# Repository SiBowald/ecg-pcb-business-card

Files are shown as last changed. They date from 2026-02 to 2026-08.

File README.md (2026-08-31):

# ECG PCB Business Card

## Table of contents

- [ECG PCB Business Card](#ecg-pcb-business-card)
  - [Intended use / disclaimer](#intended-use--disclaimer)
  - [Battery safety](#battery-safety)
  - [What the card does](#what-the-card-does)
  - [Compatibility (important)](#compatibility-important)
  - [Quick start (battery recommended)](#quick-start-battery-recommended)
  - [How to hold it (signal quality)](#how-to-hold-it-signal-quality)
  - [Powering via NFC energy harvesting (Android only)](#powering-via-nfc-energy-harvesting-android-only)
  - [What you should see](#what-you-should-see)
  - [Files & documentation](#files--documentation)
    - [Project structure](#project-structure)
    - [Running the web app locally](#running-the-web-app-locally)
  - [Quick troubleshooting](#quick-troubleshooting)
  - [Key ICs used](#key-ics-used)
  - [License](#license)
  - [Sponsorship](#sponsorship)

Educational demo: a functional single-lead ECG front end on a business-card-sized PCB.  
It streams the signal to your phone or computer using frequency-modulated ultrasound, decoded in a browser-based web app.

Goal: power it up, open the web app, and see a clean ECG-like waveform within about a minute, without any special lab setup.

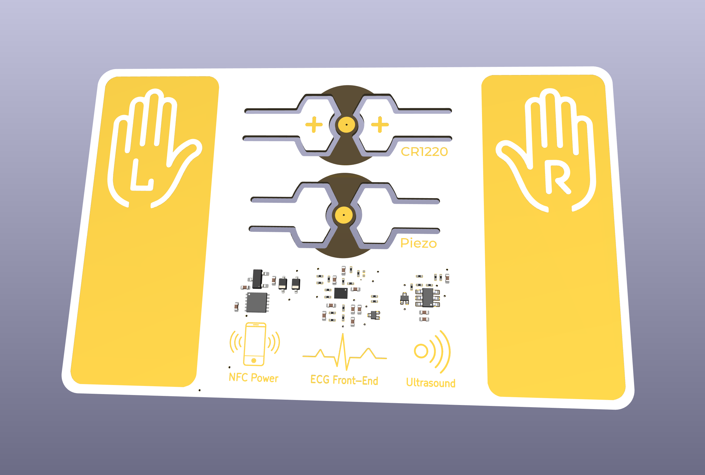
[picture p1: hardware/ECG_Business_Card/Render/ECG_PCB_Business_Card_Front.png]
ECG PCB Business Card - Front

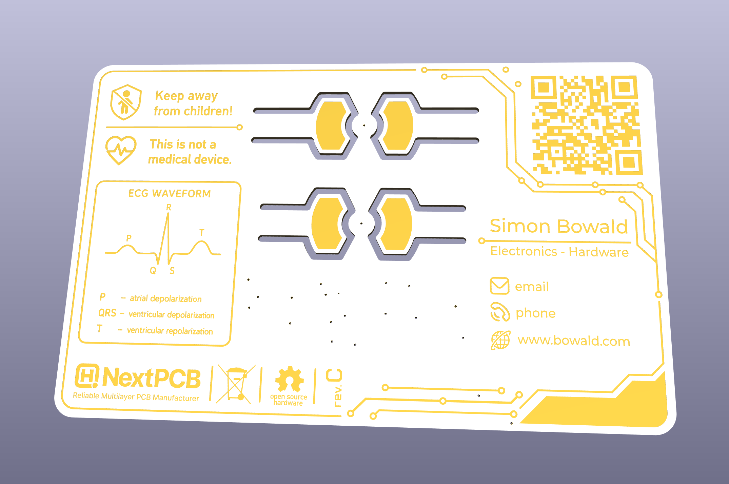
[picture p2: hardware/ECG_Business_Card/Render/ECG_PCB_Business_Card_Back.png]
ECG PCB Business Card - Front

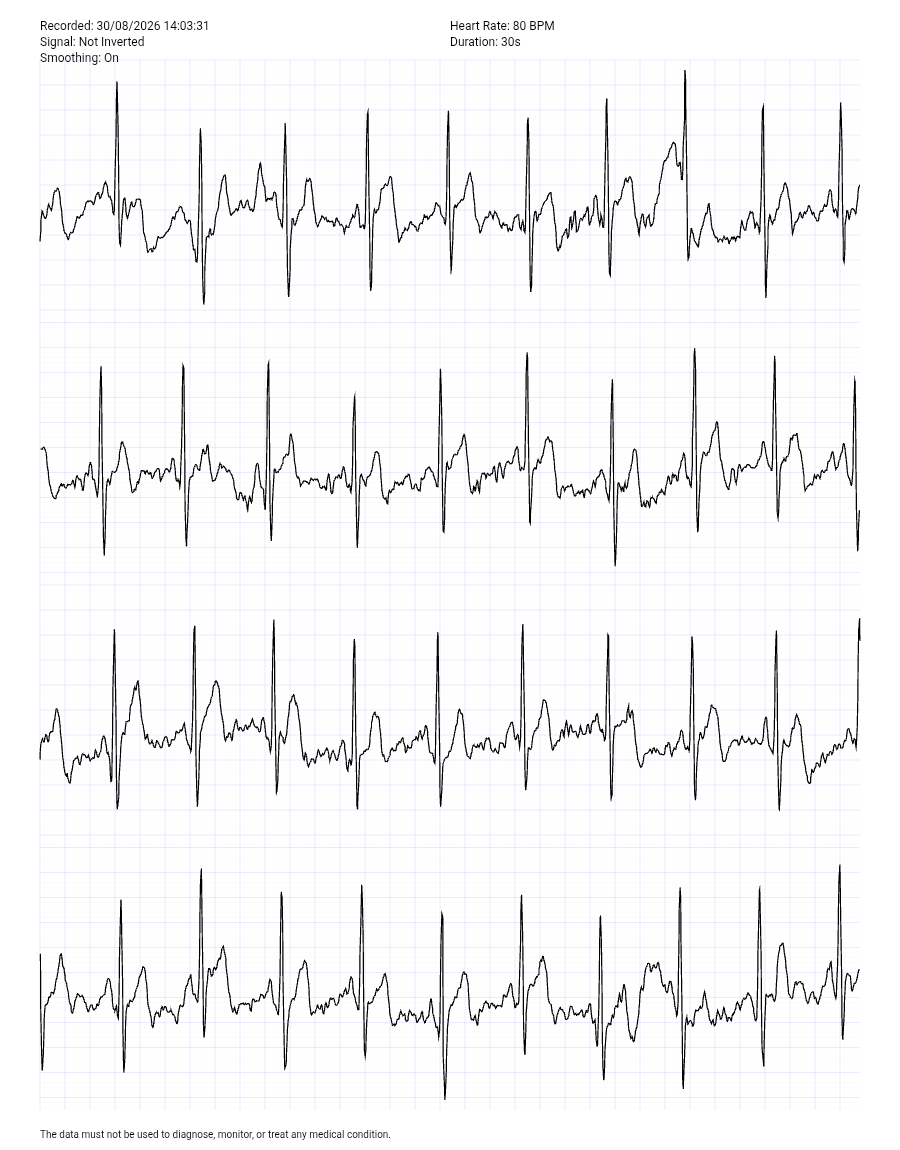
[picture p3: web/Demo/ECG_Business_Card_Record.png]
ECG PCB Business Card - Record


---

## Intended use / disclaimer

**This is a DIY educational demo and not a medical device.**  
It is not intended for diagnosis, monitoring, or clinical decisions.

---

## Battery safety

The CR1220 coin cell may be outside of its original packaging. Coin cell batteries are hazardous if swallowed, so **keep them away from children at all times**.

---

## What the card does

- Measures a single-lead ECG using the built-in left/right finger pads
- Streams the signal to a web application via **ultrasound** (microphone permission required)
- Power options:
  - **Battery (recommended)**
  - **NFC energy harvesting (Android only)**

---

## Compatibility (important)

- **iOS:** works best with **Safari**
- **Android:** works best with **Chrome**
- **NFC energy harvesting:** works **only on Android**
  - iOS does not provide a reliable continuous NFC power mode for this use
- If powering via NFC energy harvesting, the phone **must not be charging** (unplug it)

---

## Quick start (battery recommended)

1. **Insert a 3 V CR1220 battery** (rated for at least **500 µA continuous load**).  
   Ensure the **+ (positive) side** faces the same direction as the **+** symbols on the PCB.  
   Do not bend the arms of the PCB battery holder more than necessary.  
   Idle current is **below 1 µA**, so the battery can be left in the holder.

2. **Open the web app**
   - Easiest: tap the phone to the card to open the link (NFC enabled + phone unlocked)
   - Scan the printed QR code
   - Or run locally (see **Files & documentation** below)

3. **In the web application**
   - Press **Start**
   - Allow **microphone access** when prompted

---

## How to hold it (signal quality)

- Place the phone/laptop on a table and rest your elbows to reduce motion.
- Hold the card firmly and press your thumbs onto the pads:
  - Left thumb on the pad marked with the hand icon and **“L”**
  - Right thumb on the pad marked with the hand icon and **“R”**
- Stay still and relax your hands and shoulders (movement causes artifacts).
- Keep the phone close to the card so the microphone picks up the signal reliably.
- Use a quiet room if possible (avoid talking, music, fans, strong background noise).
- Avoid Bluetooth headsets so the browser uses the built-in microphone.

---

## Powering via NFC energy harvesting (Android only)

Use this when you want a “no battery” demo. It is more sensitive to positioning.

1. Make sure the phone is **not charging** (unplug it).
2. Place the card on the **back of the phone**, centered over the phone’s **NFC coil** area.
3. Flip the card upside down as needed so Left/Right orientation is correct while it sits on the phone.
4. Press fingers on the same **L** and **R** pads as in battery mode.
5. If your phone has a metal frame/back, avoid touching metal parts while contacting the pads.

---

## What you should see

You should see a waveform similar to the example printed on the back of the card (below “This is not a medical device.”).

If the signal looks noisy or flat, it is almost always due to:
- Contact pressure
- Hand motion
- Dry skin
- NFC positioning (in harvesting mode)

---

## Files & documentation

### Project structure

- `hardware/ECG_Business_Card/`  
  KiCad project including the schematic, PCB layout, manufacturing files, and documentation assets.

- `web/`  
  Browser-based ECG decoder and viewer.

### Web app

The ECG monitor can be used either locally or directly through GitHub Pages.

**Online:**  
[Open the Ultrasound-based ECG Monitor](https://sibowald.github.io/ecg-pcb-business-card/)

**Locally:**  
Open `web/ultrasound-ecg-monitor/index.html` in a modern web browser.

Microphone access is required for the ECG monitor.

---

## Quick troubleshooting

### No signal / flat line
- Confirm battery orientation (+ matches PCB)
- Press **Start**
- Ensure the browser has **microphone permission**
- Keep the phone very close and ensure it uses the **built-in mic** (disconnect Bluetooth devices)
- Audio sanity check: clapping near the phone should cause a visible change in the signal

### Very noisy signal
- Stay still, increase thumb pressure slightly, relax shoulders
- Try a quieter room
- Dry skin reduces contact: slightly moist fingertips can help
- Avoid touching metal parts of the phone while contacting the pads

### NFC power issues (Android)
- Phone must be unplugged (not charging)
- Align the card over the NFC coil and try small position shifts
- Remove thick cases

---

## Key ICs used

- **AD8233** – Single-lead ECG analog front end (instrumentation amp + filters) used to acquire the ECG signal from the finger pads.
- **LTC6990** – Timer/VCO used to generate the FM ultrasound carrier/modulation for audio-band transmission.
- **ST25DV** – NFC tag used for tap-to-open link and NFC energy harvesting support.

---

## License

See `LICENSE`.

---

## Sponsorship

### Rev. C – Supported by NextPCB

Revision C of the **ECG PCB Business Card** was kindly sponsored by **NextPCB**, who supported the PCB manufacturing and assembly of this revision.

Thank you to NextPCB for supporting this project!

<p align="center">
  <a href="https://www.nextpcb.com/">
    NextPCB
  </a>
</p>

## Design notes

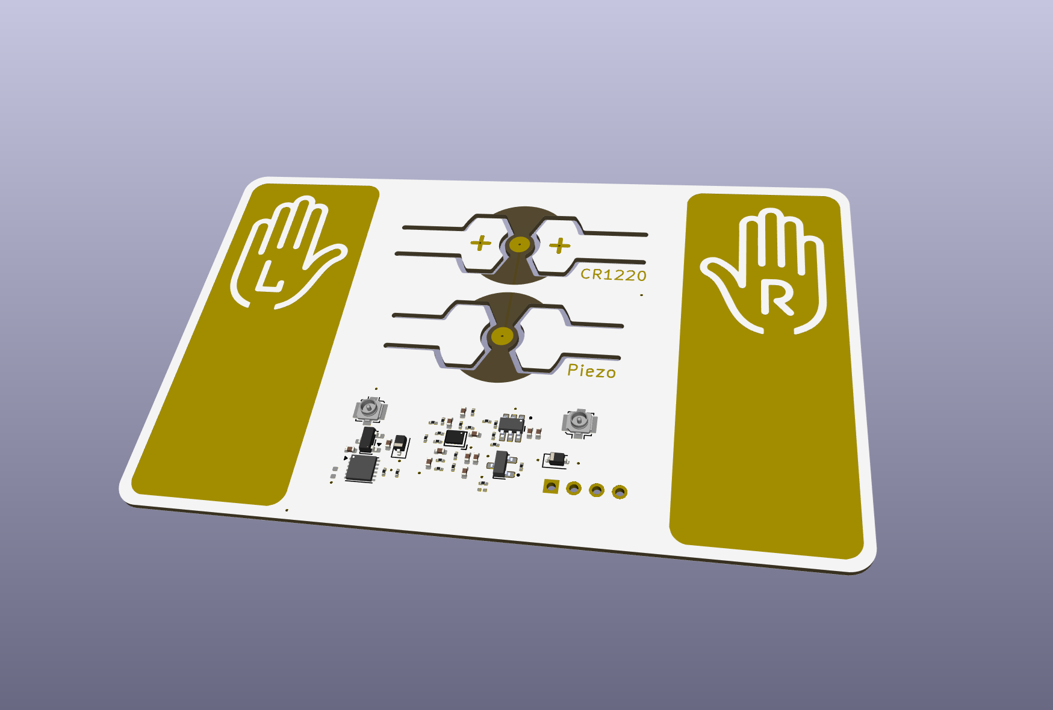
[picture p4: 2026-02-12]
hardware/ECG_Business_Card_v3/Render/ECG_PCB_Business_Card_Front.png

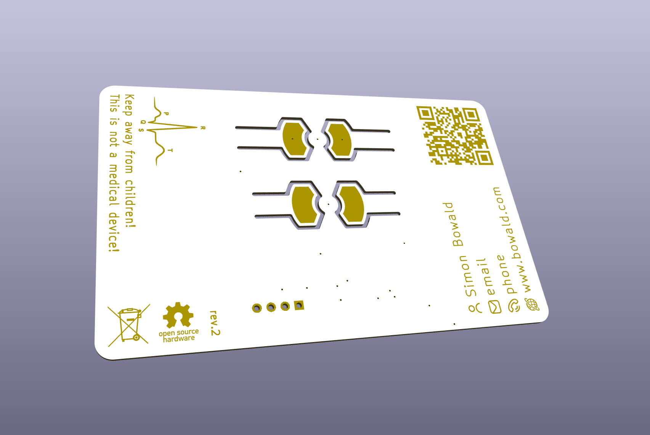
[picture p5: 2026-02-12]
hardware/ECG_Business_Card_v3/Render/ECG_PCB_Business_Card_Back.png

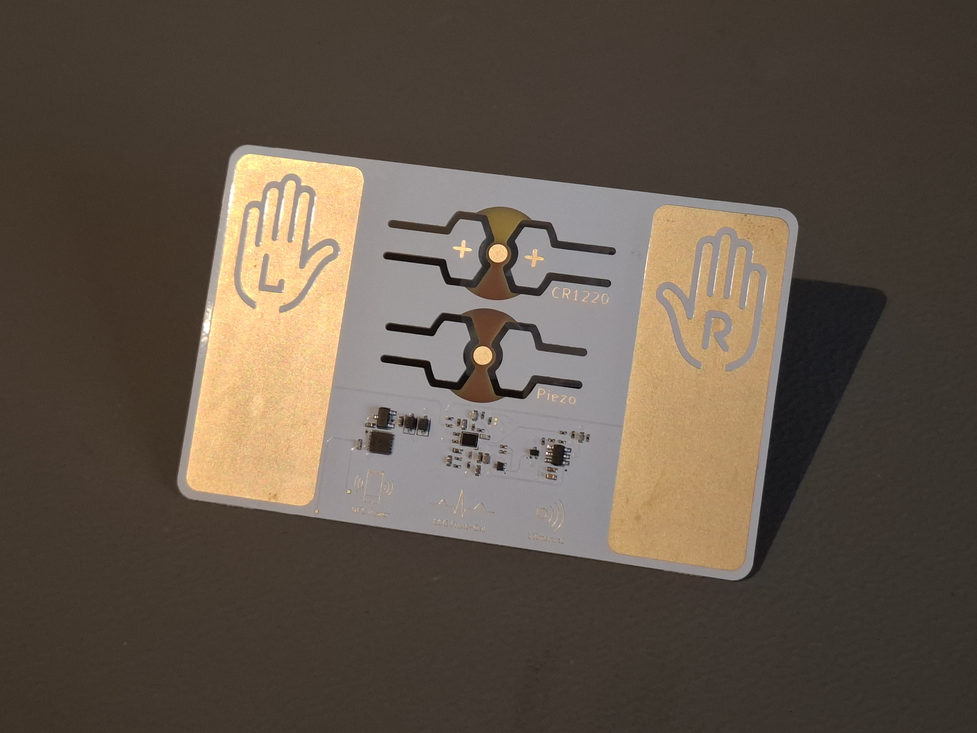
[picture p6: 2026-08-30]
hardware/ECG_Business_Card/Picutres/ecg-pcb-business-card_front_empty_revC.jpg

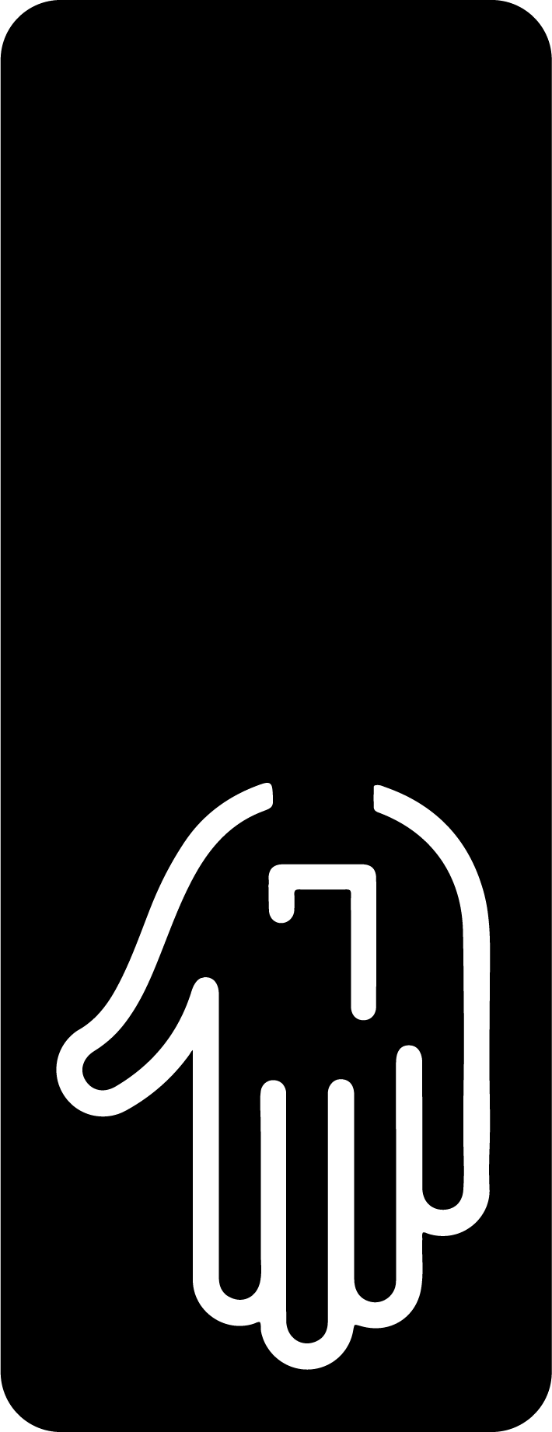
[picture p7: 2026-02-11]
hardware/ECG_Business_Card/illustrations/left_pad.png

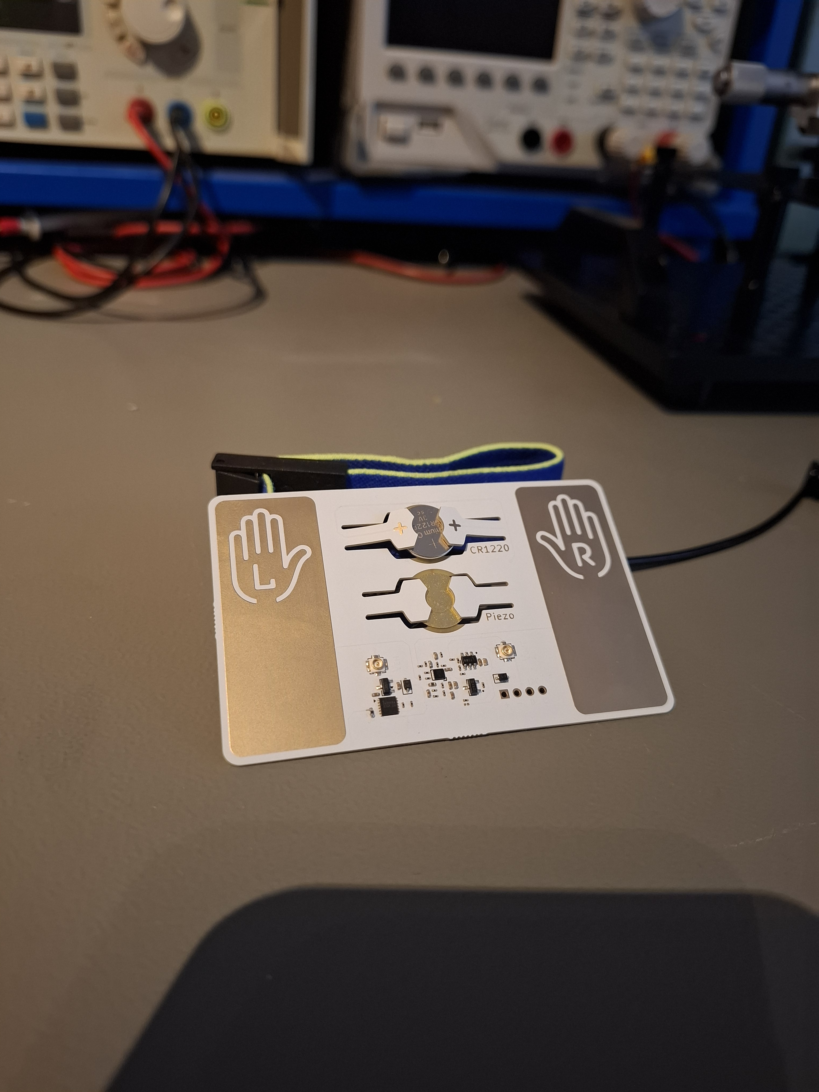
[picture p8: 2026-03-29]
hardware/ECG_Business_Card_v3/Picutres/ecg-pcb-business-card_front_1.jpg

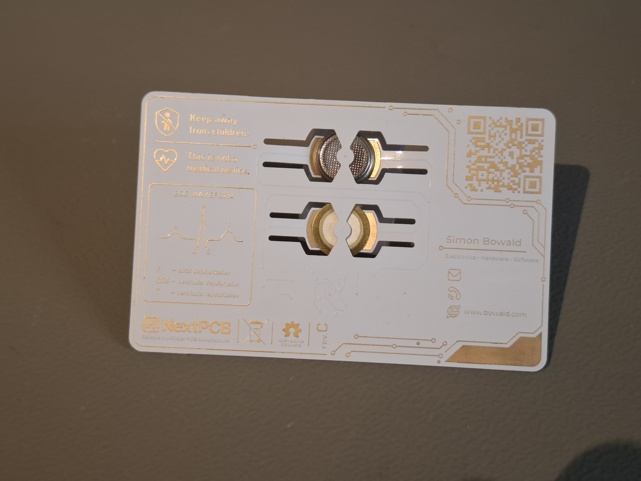
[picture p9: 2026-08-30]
hardware/ECG_Business_Card/Picutres/ecg-pcb-business-card_back_revC.jpg

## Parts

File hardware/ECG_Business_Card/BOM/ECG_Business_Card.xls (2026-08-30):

Designator* | Quantity* | Manufacturer Part Number* | Manufacturer | Package/Footprint | Description | Procurement Type | Customer Note
Required | Required | Required |  |  |  | Optional 1）Do not populate/install: DNP 2）Customer supplied part: C Learn more >
C1,C11,C13 | 3 | UN0002324 | Murata | ECG_Business_Card_Library:C_0402_1005Metric | 1uF 6.3V Ceramic Cap
C2,C10 | 2 | CA0134507 | Murata | ECG_Business_Card_Library:C_0402_1005Metric | 100nF 16V Ceramic Cap
C3 | 1 | CA0486706 | TDK | ECG_Business_Card_Library:C_0402_1005Metric | 10V 3.3uF X5R ±10% 0402 Ceramic Capacitors RoHS
C4 | 1 | CA0001023 | Murata | ECG_Business_Card_Library:C_0402_1005Metric | 220nF 16V Ceramic Cap
C5,C6 | 2 | CA0462650 | Murata | ECG_Business_Card_Library:C_0402_1005Metric | CAP CER 5.6nF 50V C0G 0402
C7,C9 | 2 | CA0134847 | Murata | ECG_Business_Card_Library:C_0402_1005Metric | 10uF 6.3V Ceramic Cap
C8,C14 | 2 | CA0134514 | Murata | ECG_Business_Card_Library:C_0402_1005Metric | 1nF 50V Ceramic Cap
C12 | 1 | CA0000500 | Murata | ECG_Business_Card_Library:C_0402_1005Metric | 6pF 50V Ceramic Cap
D1,D2 | 2 | DS0183598 | JSCJ | ECG_Business_Card_Library:SOD-123 | DIODE SCHOTTKY 30V SOD-323
Q1,Q2 | 2 | DS0075181 | Rohm Semiconductor | ECG_Business_Card_Library:SOT-723 | MOSFET P-CH 20V 200MA VMT3
R1,R2,R5,R6,R7,R11 | 6 | RE0186683 | Yageo | Resistor_SMD:R_0201_0603Metric | 10M Film Resistor ±1% 0,05W
R3,R4 | 2 | RE0016890 | Yageo | Resistor_SMD:R_0201_0603Metric | 330KΩ ±1% 1/20W ±200ppm/℃
R8,R18 | 2 | RE0024829 | Yageo | Resistor_SMD:R_0201_0603Metric | 100Ω ±1% 1/20W ±200ppm/℃
R9,R13,R14,R19,R22 | 5 | RE0015979 | Yageo | Resistor_SMD:R_0201_0603Metric | 1M Film Resistor ±1% 1/20W ±200ppm/℃
R10,R15 | 2 | RE0017187 | Yageo | Resistor_SMD:R_0201_0603Metric | 510KΩ ±1% 1/20W ±200ppm/℃
R12 | 1 | RE0347456 | Yageo | Resistor_SMD:R_0201_0603Metric | 680KΩ ±1% 1/20W ±200ppm/℃
R16 | 1 | RE0186561 | UNI-ROYAL | Resistor_SMD:R_0201_0603Metric | 2.4M Film Resistor ±1% 50mW
R17 | 1 | RE0018046 | Yageo | Resistor_SMD:R_0201_0603Metric | 82k Film Resistor ±1% 1/20W ±200ppm/℃
R20 | 1 | RE0013012 | Yageo | Resistor_SMD:R_0201_0603Metric | 0Ω ±5% 1/20W
R21 | 1 | RE0013012 | Yageo | Resistor_SMD:R_0201_0603Metric | 0Ω ±5% 1/20W | DNP
U1 | 1 | AD8233ACBZ-R7 | Analog Devices | ECG_Business_Card_Library:20-WLCPS-2MMX1.7MM | ECG Amplifier IC
U2 | 1 | IC0556188 | STMicroelectronics | ECG_Business_Card_Library:ST_UFDFPN-12-1EP_3x3mm_P0.5mm_EP1.4x2.55mm | IC RFID TRANSP 13.56MHZ 12UFDFPN (HQ: ST25DV04K-JFR8D3)
U3 | 1 | PM0185423 | MICROCHIP | Package_TO_SOT_SMD:SOT-23 | Low Quiescent Current LDO (HQ: ME6228A30M3G)
U4 | 1 | IC0466102 | Analog Devices | ECG_Business_Card_Library:SOT95P280X100-6N | Oszillator - Silizium IC 488Hz bis 2MHz (HQ: LTC6990CS6#TRPBF)

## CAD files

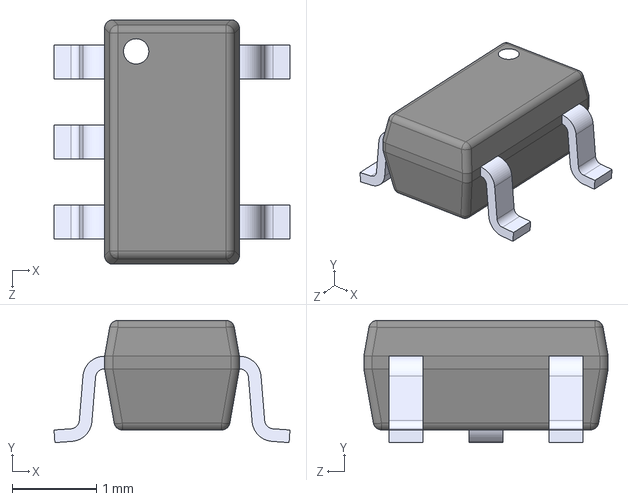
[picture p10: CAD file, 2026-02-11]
hardware/ECG_Business_Card/3dmodels/SN74LVC1G14DBVRE4.STEP
2.80 x 1.45 x 2.90 mm

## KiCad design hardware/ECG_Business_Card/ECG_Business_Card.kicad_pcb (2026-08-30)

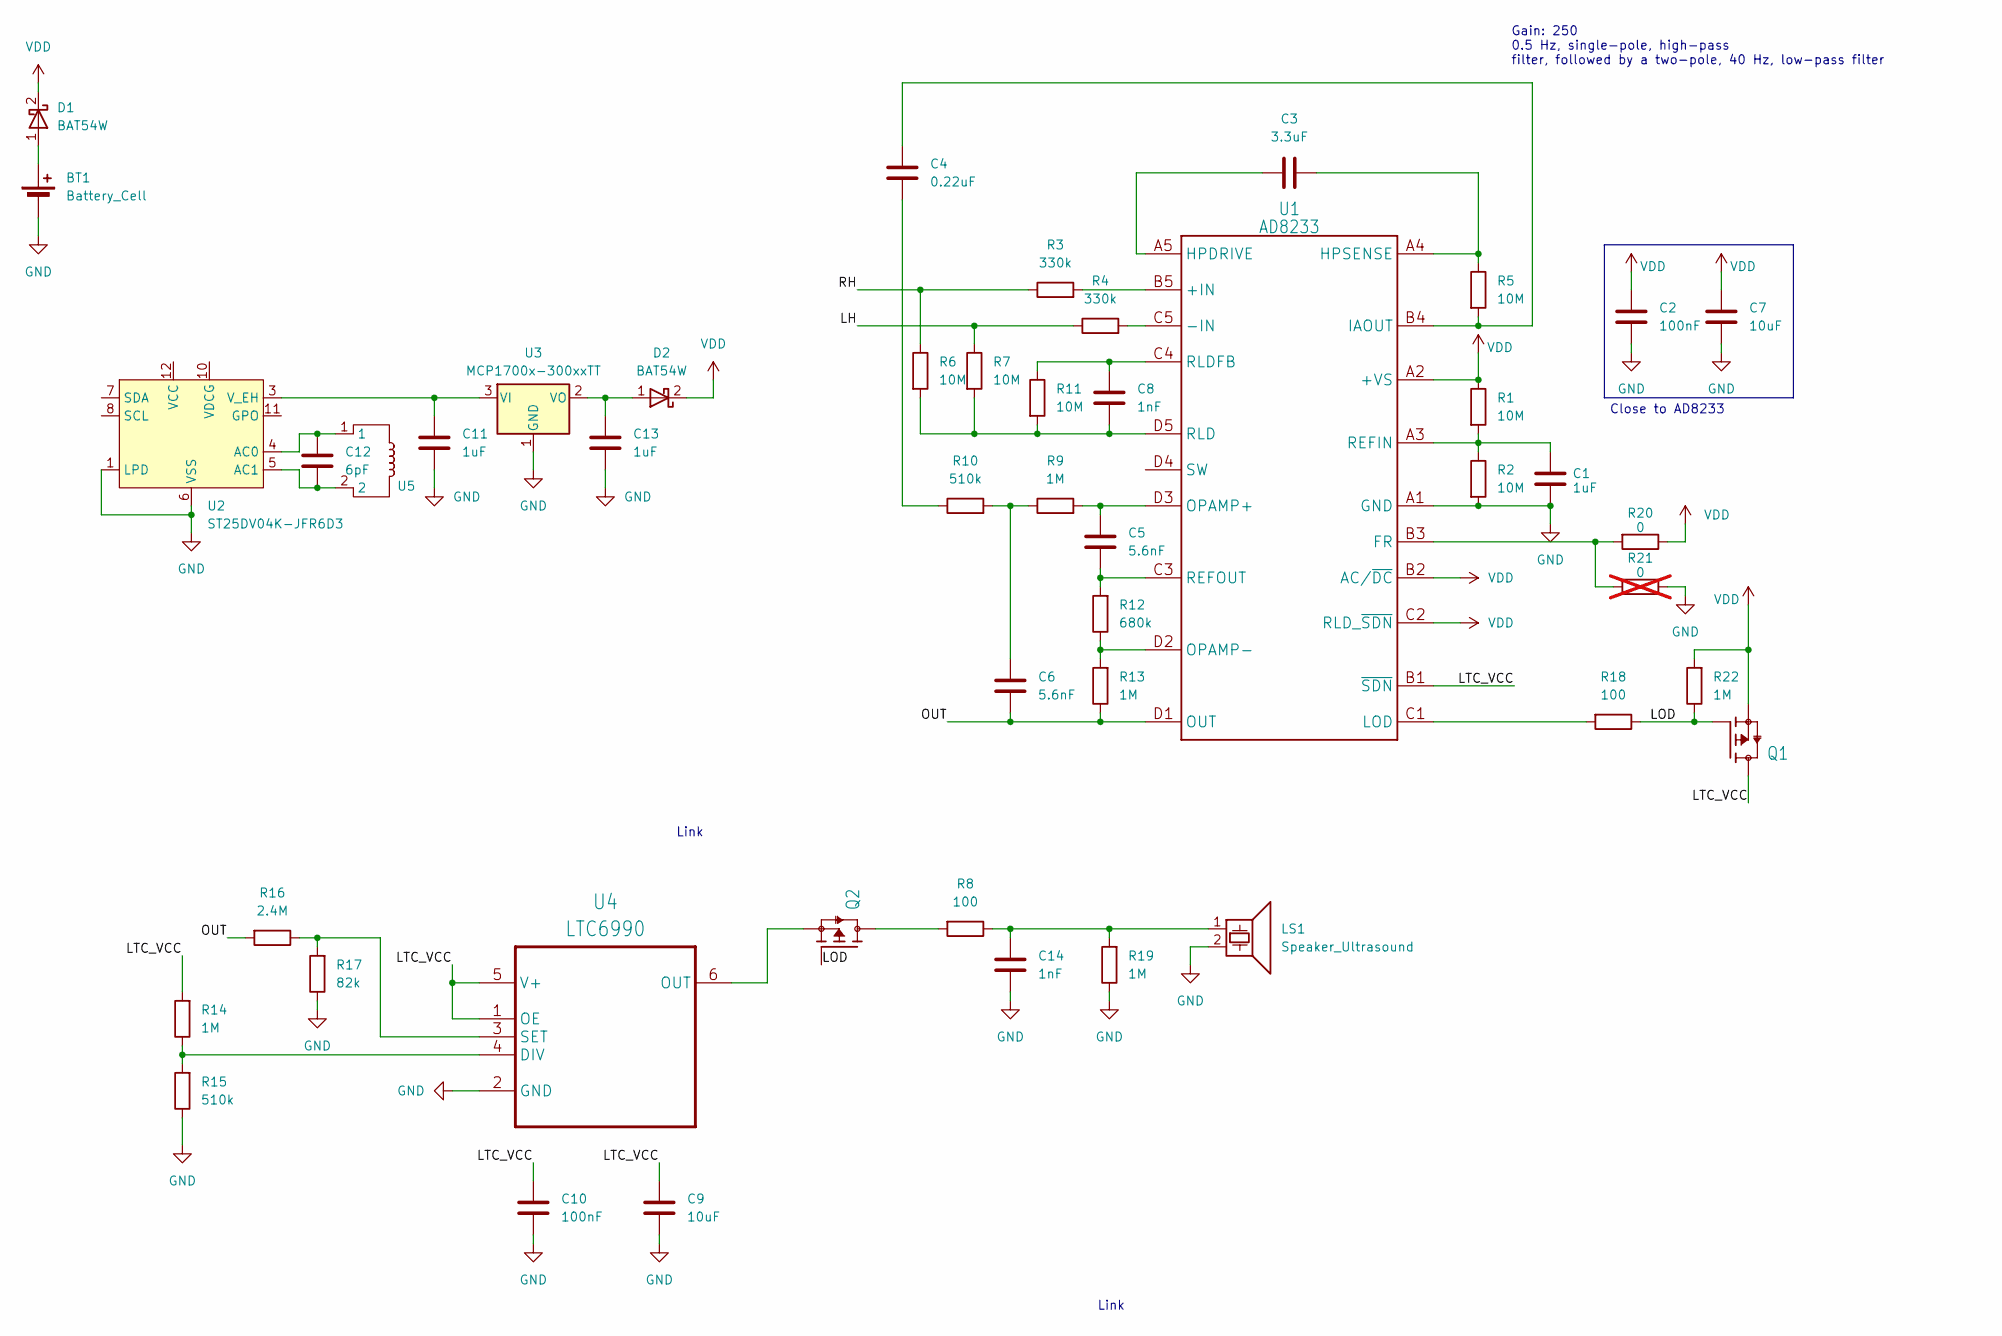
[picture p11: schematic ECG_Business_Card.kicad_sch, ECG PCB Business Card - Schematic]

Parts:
BT1: Battery_Cell; CR1220; Part Name CR1220 Battery
C1, C11, C13: 1uF; C_0402_1005Metric; Part Name 1uF 6.3V Ceramic Cap; LCSC C2167130
C2, C10: 100nF; C_0402_1005Metric; Part Name 100nF 16V Ceramic Cap; LCSC C85857
C3: 3.3uF; C_0402_1005Metric; Part Name 10V 3.3uF X5R ±10% 0402 Ceramic Capacit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; LCSC C695126
C4: 0.22uF; C_0402_1005Metric; Part Name 220nF 16V Ceramic Cap; LCSC C126524
C5, C6: 5.6nF; C_0402_1005Metric; Part Name CAP CER 5.6nF 50V C0G 0402; LCSC C3878619
C7, C9: 10uF; C_0402_1005Metric; Part Name 10uF 6.3V Ceramic Cap; LCSC C412251
C8, C14: 1nF; C_0402_1005Metric; Part Name 1nF 50V Ceramic Cap; LCSC C76947
C12: 6pF; C_0402_1005Metric; Part Name 6pF 50V Ceramic Cap; LCSC C1575
D1, D2: BAT54W; SOD-123; Part Name DIODE SCHOTTKY 30V SOD-323; LCSC C22629
LS1: Speaker_Ultrasound; Piezo_12mm; Part Name BUZZER ELEMENT STD 18.5 KHZ 12MM
Q1, Q2: MOSFET P-CH 20V 4.2A SOT23; SOT-723; Part Name MOSFET P-CH 20V 200MA VMT3
R1, R2, R5, R6, R7, R11: 10M; R_0201_0603Metric; Part Name 10M Film Resistor ±1% 0,05W; LCSC C469663
R3, R4: 330k; R_0201_0603Metric; Part Name 330KΩ ±1% 1/20W ±200ppm/℃; LCSC C142017
R8, R18: 100; R_0201_0603Metric; Part Name 100Ω ±1% 1/20W ±200ppm/℃; LCSC C77623
R9, R13, R14, R19, R22: 1M; R_0201_0603Metric; Part Name 1M Film Resistor ±1% 1/20W ±200ppm/℃; LCSC C295786
R10, R15: 510k; R_0201_0603Metric; Part Name 510KΩ ±1% 1/20W ±200ppm/℃; LCSC C295805
R12: 680k; R_0201_0603Metric; Part Name 680KΩ ±1% 1/20W ±200ppm/℃; LCSC C226598
R16: 2.4M; R_0201_0603Metric; Part Name 2.4M Film Resistor ±1% 50mW; LCSC C474580
R17: 82k; R_0201_0603Metric; Part Name 82k Film Resistor ±1% 1/20W ±200ppm/℃; LCSC C273288
R20: 0; R_0201_0603Metric; Part Name 0Ω ±5% 1/20W; LCSC C106228
R21: 0; R_0201_0603Metric; Part Name 0Ω ±5% 1/20W; LCSC C106228; not fitted
U1: AD8233; 20-WLCPS-2MMX1.7MM; Part Name ECG Amplifier IC; LCSC C209349
U2: ST25DV04K-JFR6D3; ST_UFDFPN-12-1EP_3x3mm_P0.5mm_EP1.4x2.55mm; Part Name IC RFID TRANSP 13.56MHZ 12UFDFPN (HQ: S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; LCSC C2654815
U3: MCP1700x-300xxTT; SOT-23; Part Name Low Quiescent Current LDO (HQ: ME6228A3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; LCSC C62244
U4: LTC6990; SOT95P280X100-6N; Part Name Oszillator - Silizium IC 488Hz bis 2MHz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; LCSC C581032
U5: NFC_Antenna

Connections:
/LH: R4.1, R7.1
/LOD: Q1.1 (G), Q2.1 (G), R18.1, R22.1
/LTC_VCC: C9.2, C10.2, Q1.3 (D), R14.2, U1.B1 (~SDN), U4.1 (OE), U4.5 (V+)
/OUT: C6.1, R13.1, R16.2, U1.D1 (OUT)
/RH: R3.1, R6.1
GND: BT1.2 (-), C1.1, C2.1, C7.1, C9.1, C10.1, C11.1, C13.1, C14.1, LS1.2, R2.2, R15.1, R17.1, R19.1, R21.1, U1.A1 (GND), U2.1 (LPD), U2.6 (VSS), U3.1 (GND), U4.2 (GND)
unnamed: BT1.1 (+), D1.1 (A)
unnamed: C4.1, R10.1
unnamed: C6.2, R9.1, R10.2
unnamed: C14.2, LS1.1, R8.1, R19.2
unnamed: C13.2, D2.1 (A), U3.2 (VO)
unnamed: Q2.3 (D), R8.2
unnamed: Q2.2 (S), U4.6 (OUT)
unnamed: R3.2, U1.B5 (+IN)
unnamed: R4.2, U1.C5 (-IN)
unnamed: R20.2, R21.2, U1.B3 (FR)
unnamed: C3.1, U1.A5 (HPDRIVE)
unnamed: C3.2, R5.1, U1.A4 (HPSENSE)
unnamed: C4.2, R5.2, U1.B4 (IAOUT)
unnamed: R18.2, U1.C1 (LOD)
unnamed: C5.2, R9.2, U1.D3 (OPAMP+)
unnamed: R12.1, R13.2, U1.D2 (OPAMP-)
unnamed: C1.2, R1.2, R2.1, U1.A3 (REFIN)
unnamed: C5.1, R12.2, U1.C3 (REFOUT)
unnamed: C8.1, R6.2, R7.2, R11.2, U1.D5 (RLD)
unnamed: C8.2, R11.1, U1.C4 (RLDFB)
unnamed: C12.2, U2.4 (AC0), U5.1
unnamed: C12.1, U2.5 (AC1), U5.2
unnamed: C11.2, U2.3 (V_EH), U3.3 (VI)
unnamed: R14.1, R15.2, U4.4 (DIV)
unnamed: R16.1, R17.2, U4.3 (SET)
VDD: C2.2, C7.2, D1.2 (K), D2.2 (K), Q1.2 (S), R1.1, R20.1, R22.2, U1.A2 (+VS), U1.B2 (AC/~DC), U1.C2 (RLD_~SDN)

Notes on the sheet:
Link
Close to AD8233
Gain: 250 0.5 Hz, single-pole, high-pass filter, followed by a two-pole, 40 Hz, low-pass filter

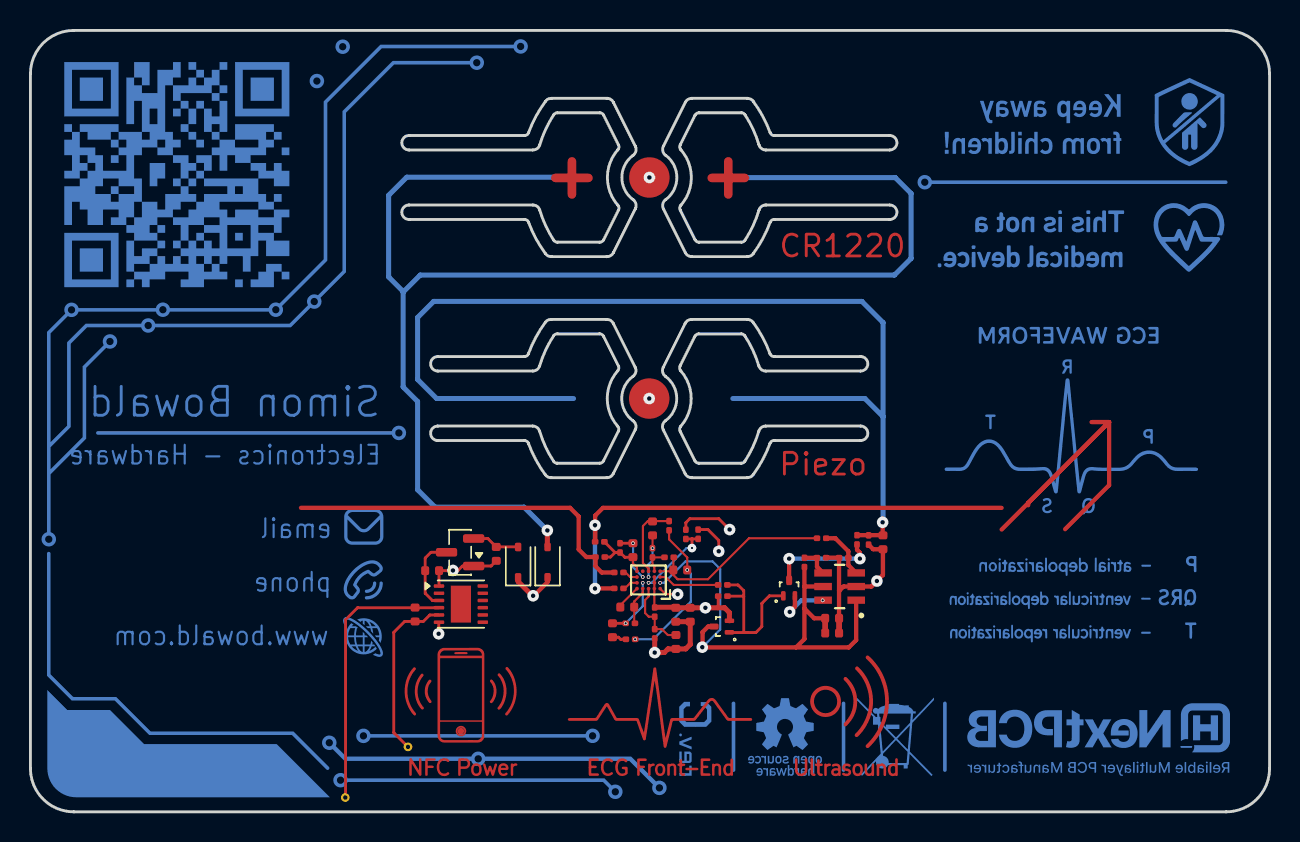
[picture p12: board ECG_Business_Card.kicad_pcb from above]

Board: 4 copper layers, 85.6 x 54.0 mm, 47 parts (0 on the bottom side), 32 nets.
